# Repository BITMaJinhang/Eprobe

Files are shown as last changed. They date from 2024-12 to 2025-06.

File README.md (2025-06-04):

# [Eprobe] Engineering Files Repository  

This repository contains engineering files for a multi-platform system, organized by functional modules to facilitate project management and collaboration.  

## Directory Structure and Descriptions  

### 1. Hardware/  
- **Content**: Hardware design engineering files  
- **Includes**:  
  - BOM — Bill of Materials (component models and quantities)  
  - PCB — PCB design diagrams  
  - Schematics — Circuit schematic diagrams  
  - 3DShell — 3D casing source files  
- **Purpose**: Reference for hardware development and manufacturing  

### 2. BLE_CH582/  
- **Content**: CH582 coprocessor firmware project  
- **Includes**:  
  - APP/ — Core functional code directory  
  - All_EVT.zip/ — All functional examples for CH58x, including firmware libraries  
- **Development Tool**: MounRiver Studio  

### 3. MCU_STM32/  
- **Content**: STM32 main processor firmware project  
- **Includes**:  
  - EprobeSTAT_V4.zip — STM32CubeIDE full project file (zipped)  
  - Core/ — Core functional code directory  
- **Development Tool**: STM32CubeIDE  

### 4. MatLabApp/  
- **Content**: MATLAB PC application project  
- **Includes**:  
  - EprobeUART.mlapp — MATLAB App Designer project file  
  - code.m — Source code for the project  
- **Development Tool**: MATLAB R20A  

### 5. MobileAPP/  
- **Content**: Mobile application project  
- **Includes**:  
  - src/ — Application source code (Vue.js)  
  - quasar.config.js — Quasar framework configuration  
  - package.json — Dependency management file  
- **Technology Stack**: Quasar + Capacitor  

## Engineering File Organization Principles  
1. Each folder corresponds to an independent functional module with complete project configurations.  
2. Standard project file formats for each platform are adopted.  
3. Hardware and software files are separated to enable collaborative development.  

## Quick Access  
- Hardware design: Directly view PDF diagrams in `Hardware/`.  
- Firmware development: Open project files via the corresponding IDE.  
- PC application debugging: Run projects as required by each platform tool.

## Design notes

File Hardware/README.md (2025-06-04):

# Hardware Design Documentation

This folder contains hardware design documentation for [Eprobe], providing supplementary information to the main thesis.

## Contents

1. **BOM File**  
   - File: [BOM_EprobeV3_2].xlsx  
   - Description: Detailed list of all hardware components, including part numbers, quantities, suppliers, and specifications.

2. **Schematic Diagram**  
   - File:
   - [SCH_EprobeV3_2_1-P1.MCU].pdf
   - [SCH_EprobeV3_2_2-P2.Power].pdf
   - [SCH_EprobeV3_2_3-P3.ADDA].pdf
   - [SCH_EprobeV3_2_4-P4.TIA_1].pdf
   - [SCH_EprobeV3_2_5-P4.TIA_2].pdf
   - [SCH_EprobeV3_2_6-P4.TIA_3].pdf
   - Description: Circuit design schematic showing component connections and signal flow.

3. **PCB Layout**  
   - File:
   - [Top Layer].pdf  
   - [Bottom Layer].pdf  
   - [Assy_Top].pdf  
   - [Assy_Bottom].pdf  
   - [Int. Plane 1].pdf  
   - [Int. Plane 2].pdf  
   - Description: Printed Circuit Board layout showing top and bottom layer traces, vias, and component placement.

4. **EasyEDA Project Files**  
   - Files: [ProDoc_Eprobe_V3_1].epro  
   - Description: Original design files created with EasyEDA, including schematic and PCB layout projects. These files can be imported into EasyEDA for editing or modification.

## Usage Instructions

1. **BOM File**  
   - Open with Microsoft Excel or compatible software.  
   - Use for procuring all necessary electronic components.

2. **Schematic Diagram**  
   - Provides detailed circuit design.  
   - Useful for analyzing circuit operation or making modifications.

3. **PCB Layout**  
   - Shows the physical arrangement of the final PCB.  
   - Helps understand component placement and board dimensions.

4. **EasyEDA Project Files**  
   - Download and import into [EasyEDA](https://pro.lceda.cn) for editing.  
   - Requires an EasyEDA account (free tier available).

## Version Information

- Current Version: v3.2

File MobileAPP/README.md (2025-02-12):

# Mobile App Development Overview

This mobile app is developed using the **Vue-quasar-capacitor** framework, targeting mobile platforms. The development environment is set up on a **MacBook Air M1** running **macOS Sequoia 15.3.1**.

## Project Configuration

- **Framework**: Vue, Quasar, Capacitor
- **Development Platform**: macOS Sequoia 15.3.1 (MacBook Air M1)

### Key Plugins

The following plugins need to be manually installed for the project to function correctly:
- **@capacitor-community/bluetooth-le**
- **vue-chartjs**

Plugin and project configuration details are available in the following files:
- `package.json`
- `package-lock.json`

## Source Code

The main source code for the app is located in the `src` folder.

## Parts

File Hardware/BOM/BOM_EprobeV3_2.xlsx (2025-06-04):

No. | Quantity | Comment | Designator | Footprint | Value | Manufacturer Part | Manufacturer | Supplier Part | Supplier
1 | 2 | 2.2uF | C1,C5 | C0402 | 2.2uF | CL05A225MQ5NSNC | SAMSUNG(三星) | C12530 | LCSC
2 | 3 | 100nF | C2,C3,C4 | C0402 | 100nF | CC0402KRX7R7BB104 | YAGEO(国巨) | C60474 | LCSC
3 | 1 | 10nF | C14 | C0402 | 10nF
4 | 1 | 22nF | C15 | C0402 | 22nF
5 | 38 | 100nF | C16,C20,C24,C28,C38,C40,C44,C50,C51,C59,C74,C75,C76,C84,C85,C86,C89,C96,C104,C105,C106,C113,C114,C115,C116,C117,C125,C126,C127,C134,C135,C136,C137,C138,C141,C142,C145,C146 | C0402 | 100nF
6 | 1 | 10uF | C17 | C0402 | 10uF | CC0402KRX7R7BB104 | YAGEO(国巨) |  | LCSC
7 | 1 | 1uF | C18 | C0402 | 1uF | CC0402KRX7R7BB104 | YAGEO(国巨) |  | LCSC
8 | 1 | 220nF | C19 | C0402 | 220nF | CC0402KRX7R7BB104 | YAGEO(国巨) |  | LCSC
9 | 6 | 33nF | C21,C60,C110,C131,C139,C143 | C0402 | 33nF
10 | 4 | 18pF | C22,C23,C72,C73 | C0402 | 18pF
11 | 12 | 100pF | C27,C31,C61,C62,C103,C111,C112,C124,C132,C133,C140,C144 | C0402 | 100pF
12 | 1 | 12pF | C45 | C0402 | 12pF | CL05A475MP5NRNC | SAMSUNG(三星) |  | LCSC
13 | 1 | 12pF | C46 | C0402 | 12pF | 0402CG120J500NT | FH(风华) | C1547 | LCSC
14 | 4 | 100nF | C47,C48,C63,C64 | C0402 | 100nF | CL05B104KB54PNC | SAMSUNG(三星) | C307331 | LCSC
15 | 1 | 4.7uF | C49 | C0402 | 4.7uF | CL05A475MP5NRNC | SAMSUNG(三星) | C23733 | LCSC
16 | 2 | 10uF | C65,C77 | C0402 | 10uF
17 | 5 | 10uF | C147,C148,C149,C150,C151 | C0402 | 10uF | CL05A106MQ5NUNC | SAMSUNG(三星) | C15525 | LCSC
18 | 7 | 10nF | C152,C153,C154,C155,C156,C157,C158 | C0402 | 10nF | CL05B103KB5NNNC | SAMSUNG(三星) | C15195 | LCSC
19 | 12 | 10uF | C159,C160,C161,C162,C163,C164,C165,C166,C167,C168,C169,C170 | C0603 | 10uF | GRM188R61E106KA73D | muRata(村田) | C344022 | LCSC
20 | 2 | 1uF | C173,C174 | C0402 | 1uF | GRM155R61H105KE05D | muRata(村田) | C1518208 | LCSC
21 | 1 | 22uF | C176 | C0402 | 22uF | GRM158R61A226ME15D | muRata(村田) | C3845593 | LCSC
22 | 6 | PJ-320D | CN3,CN4,CN5,CN6,CN7,CN8 | AUDIO-SMD_PJ-320D |  | PJ-320D | SHOU HAN(首韩) | C431535 | LCSC
23 | 9 | HC-1.0-4PWT | CN9,CN10,CN11,CN12,CN13,CN14,CN16,CN17,CN18 | CONN-SMD_4P-P1.00_HCTL_HC-1.0-4PWT |  | HC-1.0-4PWT | HCTL(华灿天禄) | C2845363 | LCSC
24 | 12 | NUP2105LT1G | D5,D6,D13,D14,D15,D16,D17,D18,D19,D20,D21,D22 | SOT-23-3_L2.9-W1.3-P1.90-LS2.4-BR |  | NUP2105LT1G | TECH PUBLIC(台舟) | C2890118 | LCSC
25 | 5 | 1N5819WS | D23,D24,D25,D26,D27 | SOD-323_L1.8-W1.3-LS2.5-RD |  | 1N5819WS | Hottech(合科泰) | C191023 | LCSC
26 | 1 | SRV05-4 | D28 | SOT-23-6_L2.9-W1.6-P0.95-LS2.8-BL-1 |  | SRV05-4 | 宏迦橙 | C7420376 | LCSC
27 | 4 | BLM18AG601SN1D | L1,L2,L4,L6 | L0603 |  | BLM18AG601SN1D | muRata(村田) | C19330 | LCSC
28 | 2 | 10uH | L9,L10 | IND-SMD_L4.4-W4.2_BCIHP0412SC | 10uH | BCIHP0420SC-100M | BC(台湾诚阳) | C2921170 | LCSC
29 | 1 | LED_0603-R | LED2 | LED_0603
30 | 1 | LED_0603-G | LED3 | LED_0603
31 | 2 | NCD0603G1 | LED4,LED6 | LED0603-RD |  | NCD0603G1 | 国星光电 | C84267 | LCSC
32 | 1 | NCD0603B1 | LED5 | LED0603-RD |  | NCD0603B1 | 国星光电 | C84266 | LCSC
33 | 1 | AO3401A | Q1 | SOT-23_L2.9-W1.3-P1.90-LS2.4-BR |  | AO3401A | AOS | C15127 | LCSC
34 | 13 | 10kΩ | R2,R3,R16,R53,R55,R100,R103,R132,R133,R141,R142,R171,R172 | R0402 | 10kΩ
35 | 2 | 390K | R5,R9 | R0402 | 390K
36 | 1 | 33K | R6 | R0402 | 33K
37 | 1 | 3.1kΩ | R17 | R0402 | 3.1kΩ
38 | 6 | 750Ω | R18,R94,R140,R179,R183,R187 | R0402 | 750Ω
39 | 12 | 2kΩ | R19,R20,R63,R87,R134,R135,R173,R174,R180,R181,R184,R185 | R0402 | 2kΩ
40 | 1 | 10kΩ | R24 | R0402 | 10kΩ | 0402WGF1003TCE | UNI-ROYAL(厚声) |  | LCSC
41 | 1 | 100Ω | R26 | R0402 | 100Ω
42 | 11 | 10K | R27,R43,R59,R60,R65,R66,R239,R242,R245,R248,R251 | R0402 | 10K
43 | 6 | 3.9K | R28,R240,R243,R246,R249,R252 | R0402 | 3.9K
44 | 6 | 2K | R29,R241,R244,R247,R250,R253 | R0402 | 2K
45 | 7 | 2.2K | R30,R42,R93,R139,R178,R182,R186 | R0402 | 2.2K
46 | 3 | 5.1K | R39,R40,R41 | R0402 | 5.1K
47 | 1 | 4.7K | R49 | R0402 | 4.7K
48 | 1 | 15K | R50 | R0402 | 15K
49 | 1 | 33kΩ | R54 | R0402 | 33kΩ | 0402WGF1542TCE | UNI-ROYAL(厚声) |  | LCSC
50 | 1 | 51kΩ | R56 | R0402 | 51kΩ | 0402WGF1203TCE | UNI-ROYAL(厚声) |  | LCSC
51 | 1 | 2kΩ | R57 | R0402 | 2kΩ | RC0402FR-075KL | YAGEO(国巨) |  | LCSC
52 | 1 | 10kΩ | R58 | R0402 | 10kΩ | RC0402FR-0710KL | YAGEO(国巨) | C60490 | LCSC
53 | 1 | 33kΩ | R61 | R0402 | 33kΩ
54 | 1 | 3.9kΩ | R62 | R0402 | 3.9kΩ
55 | 3 | 5.1kΩ | R64,R188,R189 | R0402 | 5.1kΩ | 0402WGF1003TCE | UNI-ROYAL(厚声) |  | LCSC
56 | 6 | 1kΩ | R190,R212,R218,R224,R230,R236 | R0402 | 1kΩ | 0402WGF5101TCE | UNI-ROYAL(厚声) |  | LCSC
57 | 6 | 10kΩ | R191,R213,R219,R225,R231,R237 | R0402 | 10kΩ | 0402WGF2202TCE | UNI-ROYAL(厚声) |  | LCSC
58 | 6 | 750Ω | R192,R214,R220,R226,R232,R238 | R0402 | 750Ω | 0402WGF2001TCE | UNI-ROYAL(厚声) |  | LCSC
59 | 1 | 0 | R208 | R0402 | 0
60 | 1 | TS-1088R-02026 | SW1 | SW-SMD_L3.9-W3.0-P4.45 |  | TS-1088R-02026 | XUNPU(讯普) | C455280 | LCSC
61 | 1 | MSK12C02 | SW3 | SW-TH_MSK12C02 |  | MSK12C02 | SHOU HAN(首韩) | C431540 | LCSC
62 | 1 | TS-1088-AR02016 | SW4 | SW-SMD_L3.9-W3.0-P4.45 |  | TS-1088-AR02016 | XUNPU(讯普) | C720477 | LCSC
63 | 2 | M2螺丝 | TP1,TP2 | M2螺丝
64 | 1 | CH582F | U1 | QFN-28_L4.0-W4.0-P0.40-BL-EP2.8 |  | CH582F | WCH(南京沁恒) | C3001175 | LCSC
65 | 1 | STM32L432KCU6 | U2 | UFQFPN-32_L5.0-W5.0-P0.50-TL-EP3.5 |  | STM32L432KCU6 | ST(意法半导体) | C1337280 | LCSC
66 | 1 | DAC8568ICPWR | U3 | TSSOP-16_L5.0-W4.4-P0.65-LS6.4-BL |  | DAC8568ICPWR | TI(德州仪器) | C524819 | LCSC
67 | 1 | DG409DQ-T1-E3 | U4 | TSSOP-16_L5.0-W4.4-P0.65-LS6.4-BL |  | DG409DQ-T1-E3 | VISHAY(威世) | C2673358 | LCSC
68 | 6 | OPA4197QPWRQ1 | U6,U7,U8,U9,U16,U41 | TSSOP-14_L5.0-W4.4-P0.65-LS6.4-BL |  | OPA4197QPWRQ1 | TI(德州仪器) | C4366710 | LCSC
69 | 1 | TP4056 | U12 | ESOP-8_L4.9-W3.9-P1.27-LS6.0-BL-EP |  | TP4056 | UMW(友台半导体) | C725790 | LCSC
70 | 1 | SGM2036-3.3YN5G/TR | U15 | SOT-23-5_L3.0-W1.7-P0.95-LS2.8-BR |  | SGM2036-3.3YN5G/TR | SGMICRO(圣邦微) | C92402 | LCSC
71 | 2 | ADS1256IDBR | U20,U30 | SSOP-28_L10.2-W5.3-P0.65-LS7.8-BL |  | ADS1256IDBR | TI(德州仪器) | C28186 | LCSC
72 | 1 | 嘉立创二维码5x5 | U21 | JLC-QRCODE-5x5
73 | 2 | MT3608L | U22,U27 | SOT-23-6_L2.9-W1.7-P0.95-LS2.8-BL |  | MT3608L | 西安航天民芯 | C2932326 | LCSC
74 | 2 | TPS7A4901DGNT | U25,U26 | MSOP-8_L3.0-W3.0-P0.65-LS4.9-BL-EP1.8 |  | TPS7A4901DGNT | TI(德州仪器) | C61422 | LCSC
75 | 1 | TPS7A3001DGNR | U28 | MSOP-8_L3.0-W3.0-P0.65-LS5.0-BL-EP |  | TPS7A3001DGNR | TI(德州仪器) | C33835 | LCSC
76 | 1 | BWU.FL-IPEX1 | U29 | IPEX-SMD_BWIPX-1-001E |  | BWU.FL-IPEX1 | BAT WIRELESS(蝙蝠无线) | C5137195 | LCSC
77 | 1 | REF5025AIDR | U31 | SOIC-8_L4.9-W3.9-P1.27-LS6.0-BL |  | REF5025AIDR | TI(德州仪器) | C11341 | LCSC
78 | 1 | 32MHz | U42 | CRYSTAL-SMD_4P-L2.0-W1.6-BL-2 | 32MHz | XL7EL89COI-111YLC-32M | YXC(扬兴晶振) | C2965584 | LCSC
79 | 1 | WAFER-SH1.0-2PWB | U43 | CONN-SMD_2P-P1.00_XUNPU_WAFER-SH1.0-2PWB |  | WAFER-SH1.0-2PWB | XUNPU(讯普) | C3029341 | LCSC
80 | 1 | WAFER-SH1.0-3PWB | U44 | CONN-SMD_3P-P1.00_WAFER-SH1.0-3PWB |  | WAFER-SH1.0-3PWB | XUNPU(讯普) | C3029342 | LCSC
81 | 1 | KH-TYPE-C-16P | USB1 | USB-C-SMD_KH-TYPE-C-16P |  | KH-TYPE-C-16P | kinghelm(金航标) | C709357 | LCSC
82 | 2 | 8MHz | X5,X7 | OSC-SMD_4P-L3.2-W2.5-BL | 8MHz | X32258MOB4SI | YXC(扬兴晶振) | C2682775 | LCSC
83 | 1 | 32.768kHz | X6 | OSC-SMD_L3.2-W1.5 | 32.768kHz | X321532768KGD2SI | YXC(扬兴晶振) | C620155 | LCSC

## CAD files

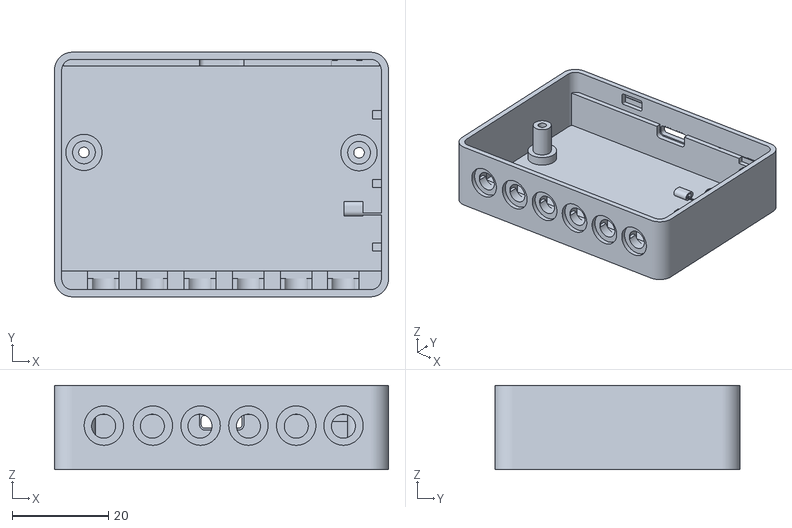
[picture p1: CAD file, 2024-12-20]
Hardware/3DShell_EprobeV3_1/3DShell_Eprobe_V3_1_B.stl
69.6 x 51.0 x 17.5

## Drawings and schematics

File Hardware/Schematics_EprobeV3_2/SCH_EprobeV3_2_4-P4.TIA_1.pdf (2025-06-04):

# S4b 10 S3b 11 S2b 12 S1b 13 V+ 14 GND 15 A1 16

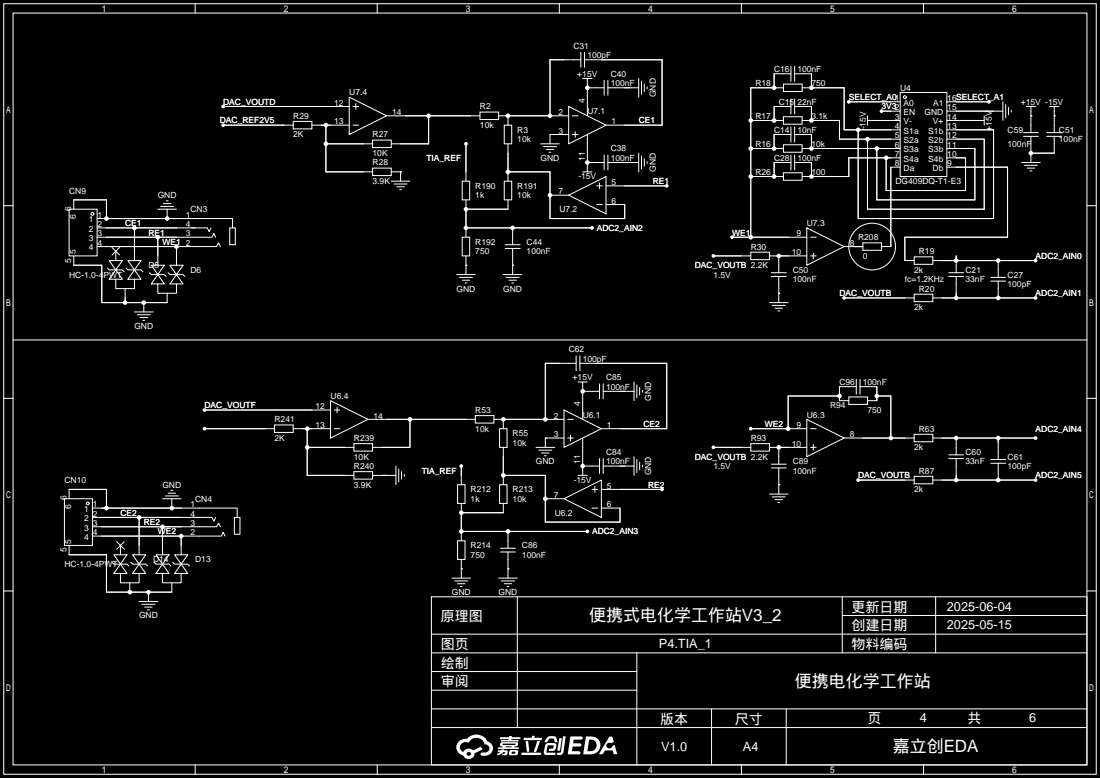
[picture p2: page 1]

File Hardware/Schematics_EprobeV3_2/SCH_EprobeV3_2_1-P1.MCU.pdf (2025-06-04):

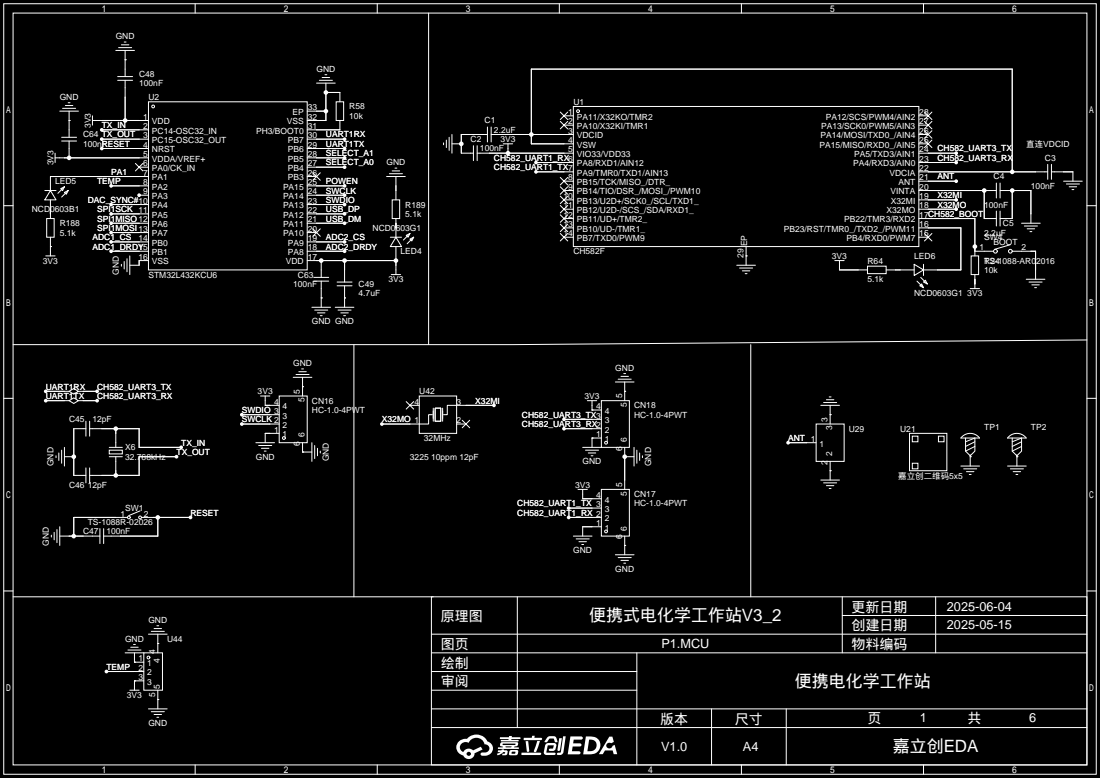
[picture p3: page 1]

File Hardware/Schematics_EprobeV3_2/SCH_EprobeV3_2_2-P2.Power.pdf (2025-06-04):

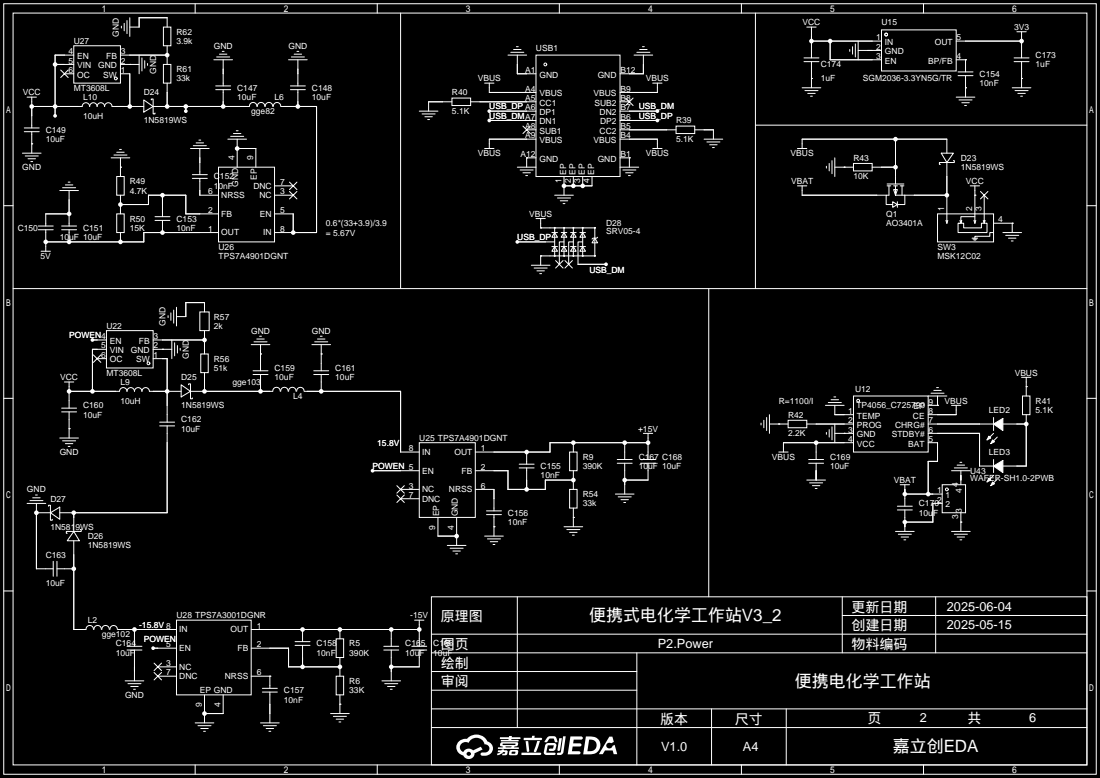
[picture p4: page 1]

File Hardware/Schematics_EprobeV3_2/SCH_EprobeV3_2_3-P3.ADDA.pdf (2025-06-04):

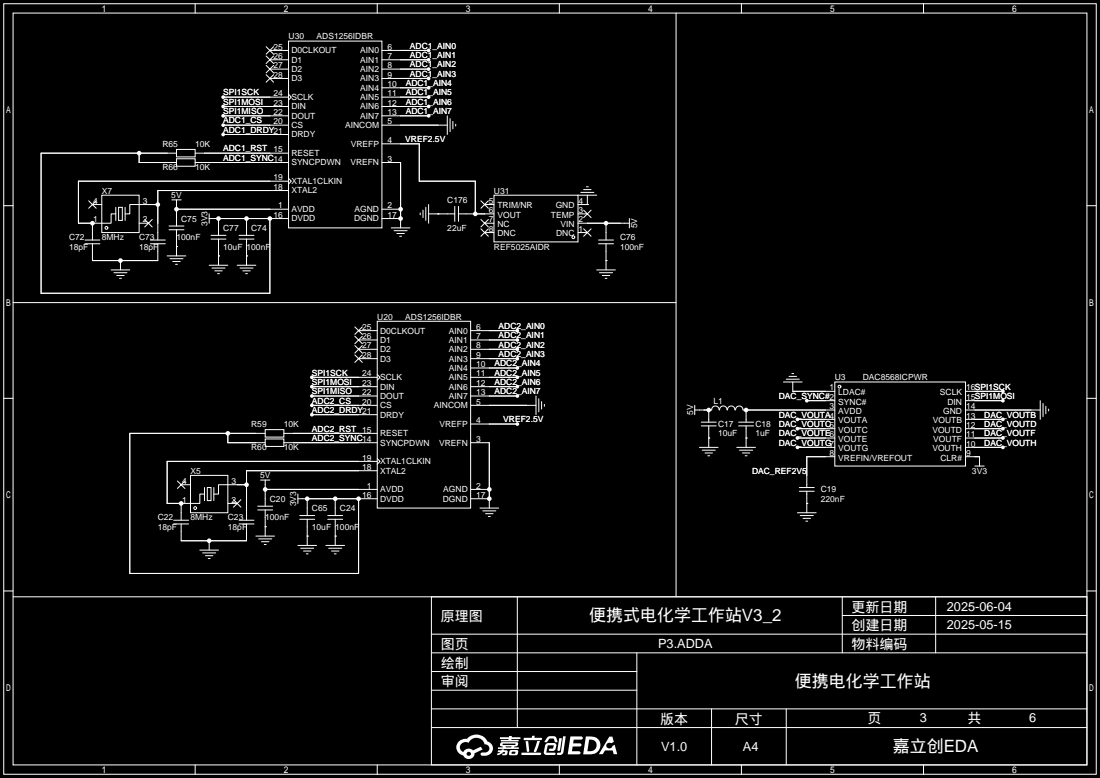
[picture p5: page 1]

VOUTH 10 VOUTF 11 VOUTD 12 VOUTB 13 GND 14 DIN 15 SCLK 16

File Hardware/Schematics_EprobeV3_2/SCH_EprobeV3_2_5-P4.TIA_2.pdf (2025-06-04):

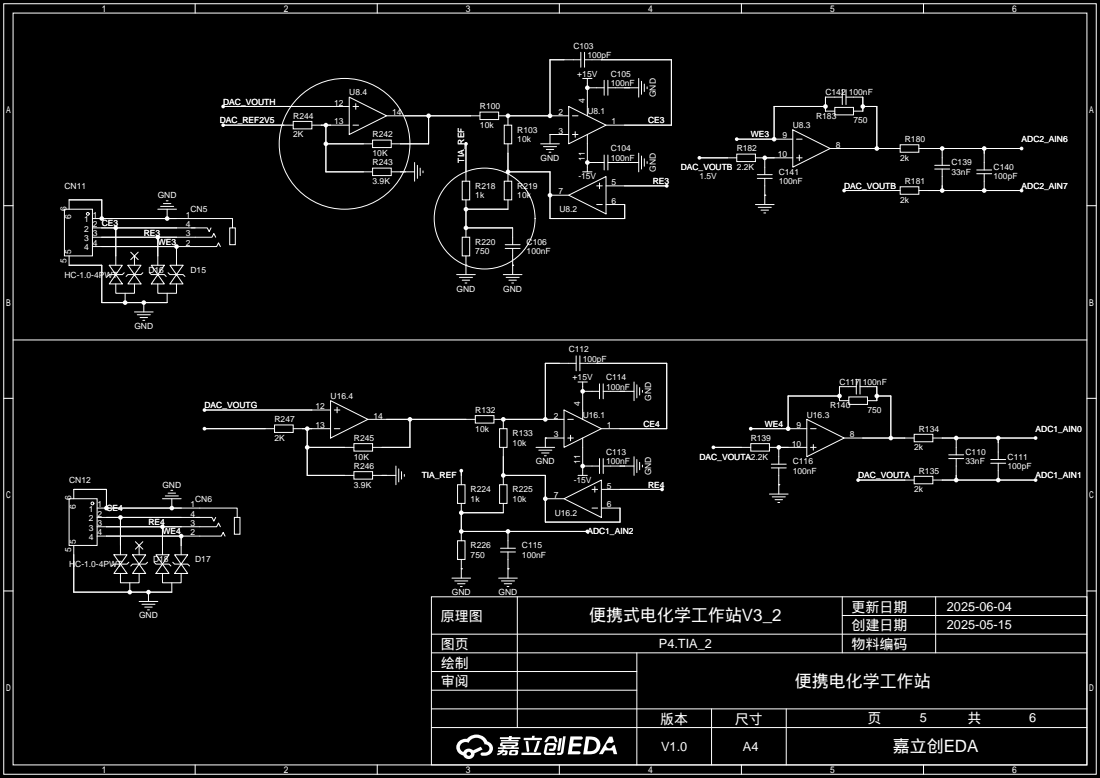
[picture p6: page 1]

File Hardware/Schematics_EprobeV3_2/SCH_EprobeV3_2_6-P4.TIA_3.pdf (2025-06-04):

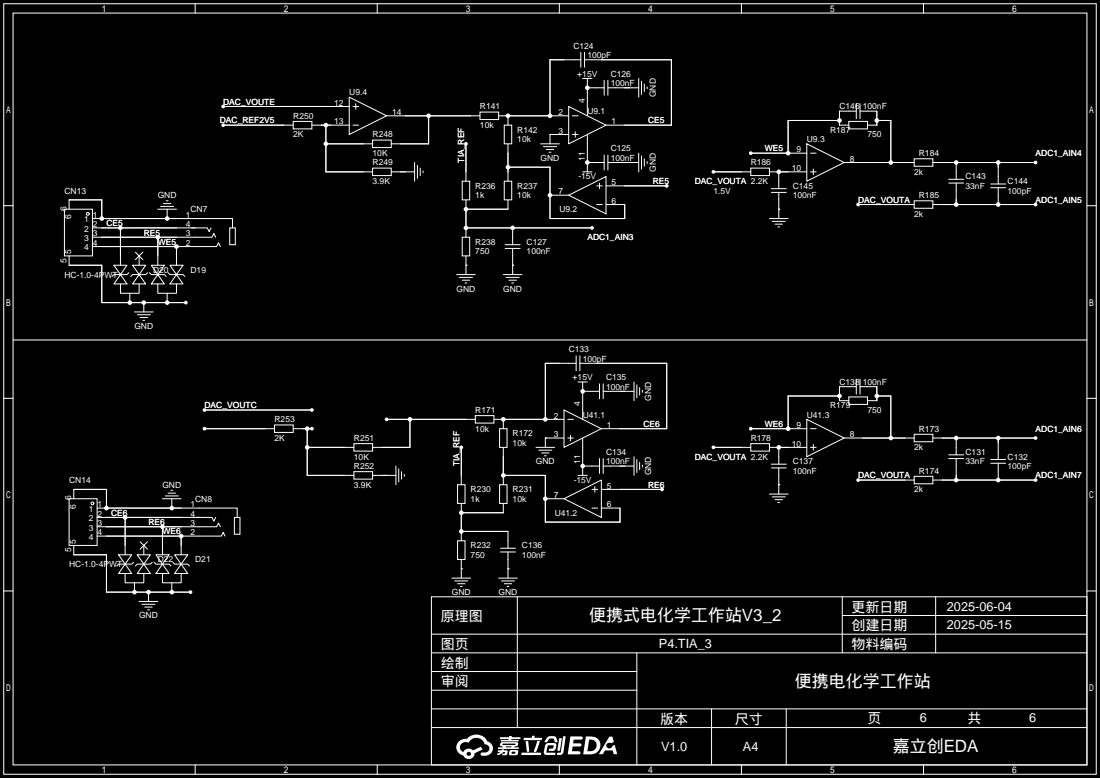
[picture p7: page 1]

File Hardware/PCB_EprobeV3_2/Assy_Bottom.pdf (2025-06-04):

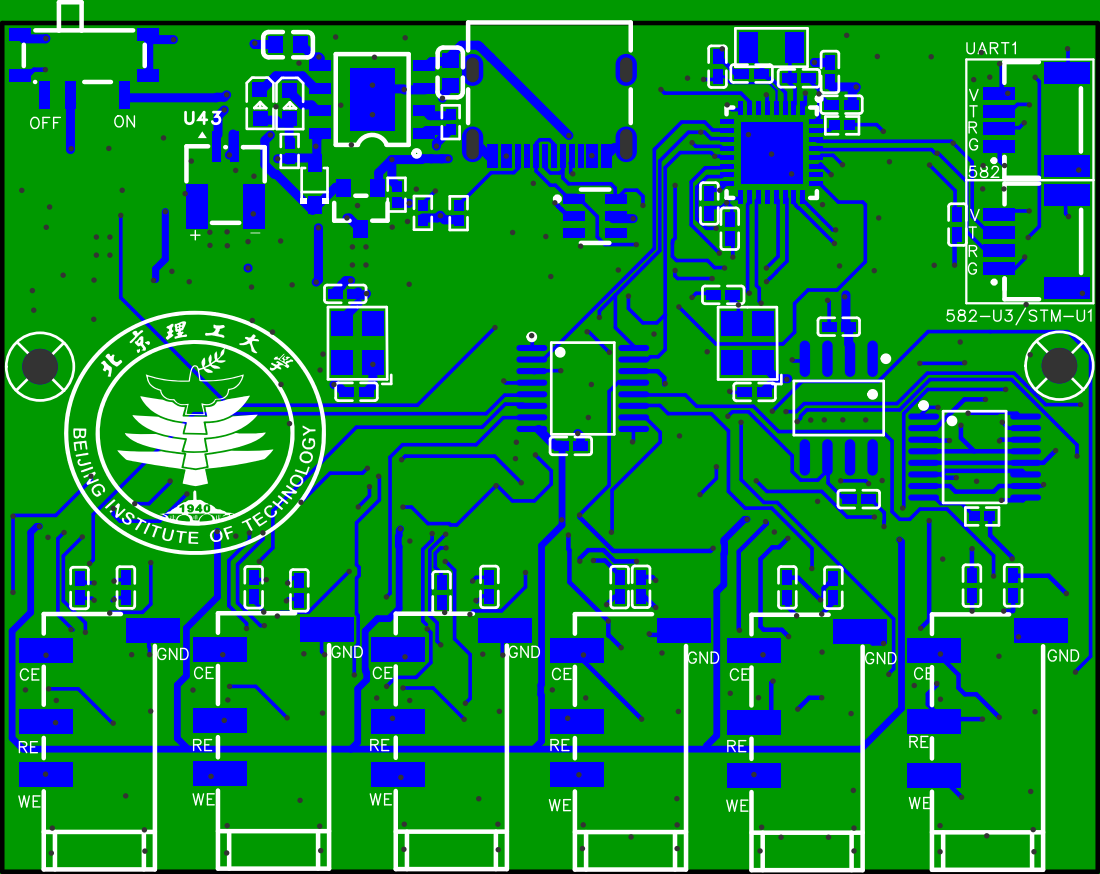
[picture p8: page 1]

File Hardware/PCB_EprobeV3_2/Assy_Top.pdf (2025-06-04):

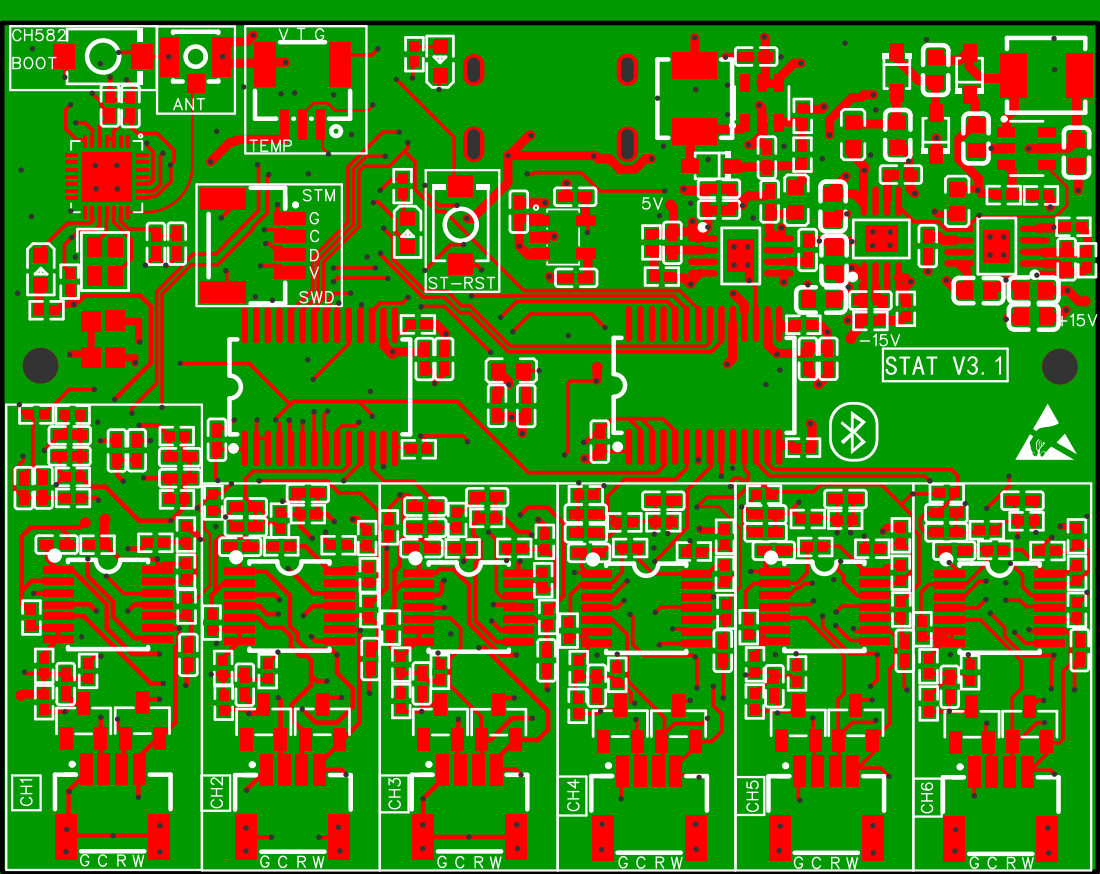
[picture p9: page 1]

CH582 BOOT | ANT | V G T

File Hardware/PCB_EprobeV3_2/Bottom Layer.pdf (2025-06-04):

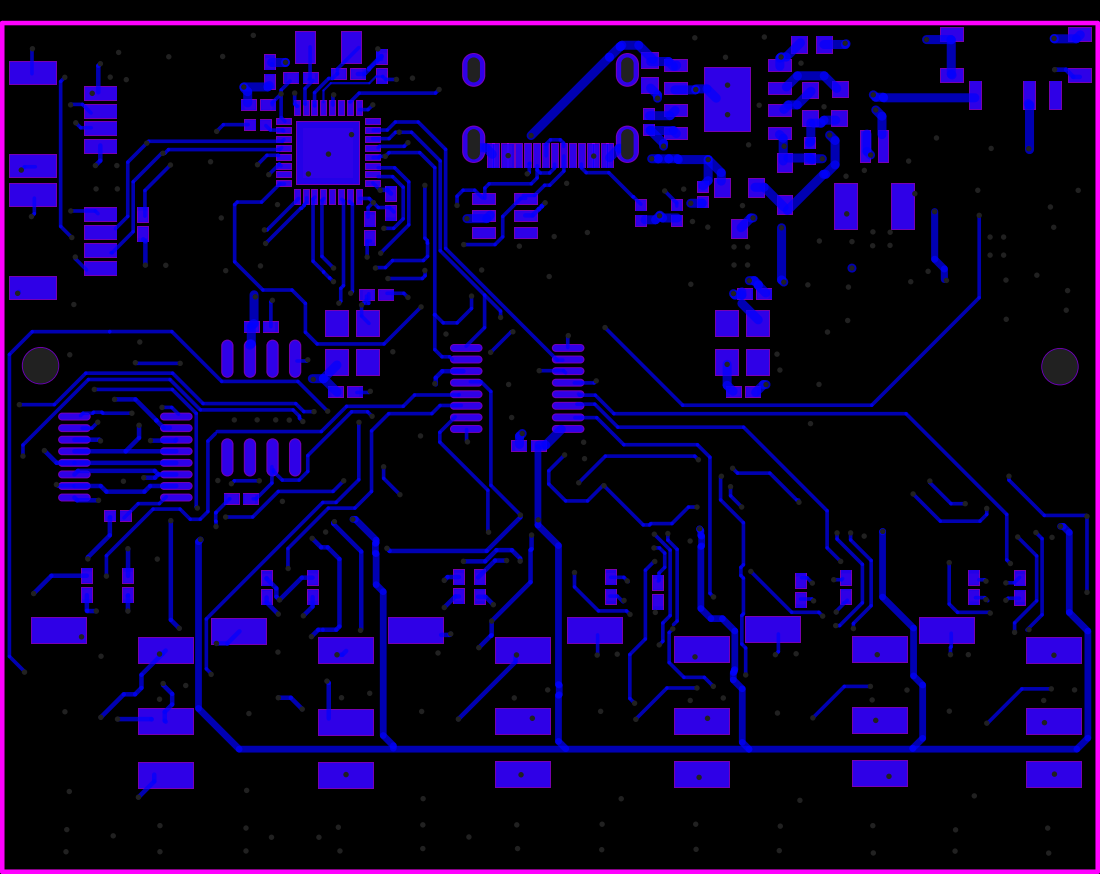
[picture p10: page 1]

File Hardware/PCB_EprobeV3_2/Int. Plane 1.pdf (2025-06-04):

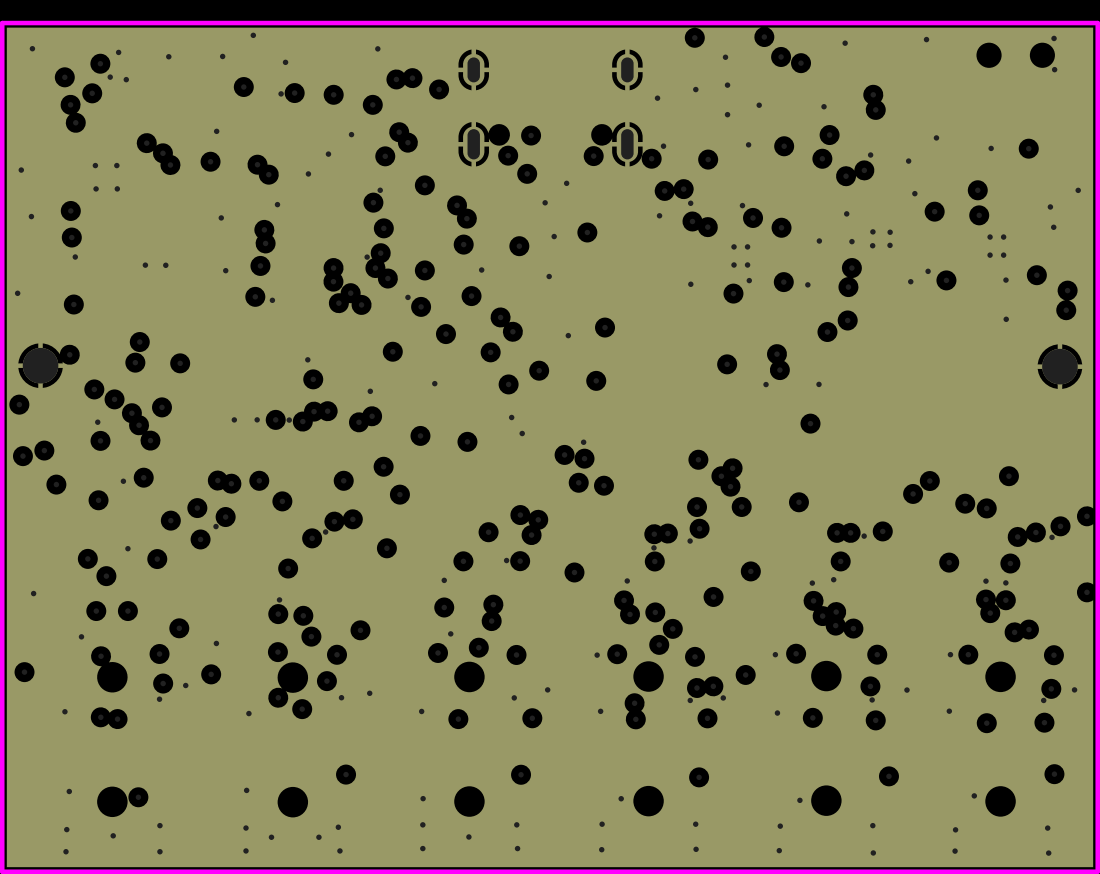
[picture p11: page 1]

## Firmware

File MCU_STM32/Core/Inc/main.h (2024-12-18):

/* USER CODE BEGIN Header */
/**
  ******************************************************************************
  * @file           : main.h
  * @brief          : Header for main.c file.
  *                   This file contains the common defines of the application.
  ******************************************************************************
  * @attention
  *
  * Copyright (c) 2024 STMicroelectronics.
  * All rights reserved.
  *
  * This software is licensed under terms that can be found in the LICENSE file
  * in the root directory of this software component.
  * If no LICENSE file comes with this software, it is provided AS-IS.
  *
  ******************************************************************************
  */
/* USER CODE END Header */

/* Define to prevent recursive inclusion -------------------------------------*/
#ifndef __MAIN_H
#define __MAIN_H

#ifdef __cplusplus
extern "C" {
#endif

/* Includes ------------------------------------------------------------------*/
#include "stm32l4xx_hal.h"

/* Private includes ----------------------------------------------------------*/
/* USER CODE BEGIN Includes */
#if defined(STM32F1)
#include "stm32f1xx_hal.h"
#include "stm32f1xx_hal_spi.h"
#elif defined(STM32F4)
#include "stm32f4xx_hal.h"
#include "stm32f4xx_hal_spi.h"
#elif defined(STM32L4)
#include "stm32l4xx_hal.h"
#include "stm32l4xx_hal_spi.h"
#include "stm32l4xx_hal_dma.h"
#elif defined(STM32F3)
#include "stm32f3xx_hal.h"
#include "stm32f3xx_hal_spi.h"
#endif
#include <stdint.h>
#include <stdio.h>
#include <stdlib.h>
#include <stdbool.h>
#include <math.h>
#include <string.h>
#include "ads125x.h"
#include "dac856x.h"
#include "eprobe.h"
#include "ble.h"
#include "ds18b20.h"

/* USER CODE END Includes */

/* Exported types ------------------------------------------------------------*/
/* USER CODE BEGIN ET */

/* USER CODE END ET */

/* Exported constants --------------------------------------------------------*/
/* USER CODE BEGIN EC */

/* USER CODE END EC */

/* Exported macro ------------------------------------------------------------*/
/* USER CODE BEGIN EM */

/* USER CODE END EM */

/* Exported functions prototypes ---------------------------------------------*/
void Error_Handler(void);

/* USER CODE BEGIN EFP */

/* USER CODE END EFP */

/* Private defines -----------------------------------------------------------*/
#define LED_Pin GPIO_PIN_1
#define LED_GPIO_Port GPIOA
#define TEMP_Pin GPIO_PIN_2
#define TEMP_GPIO_Port GPIOA
#define DAC_SYNC__Pin GPIO_PIN_4
#define DAC_SYNC__GPIO_Port GPIOA
#define ADC1_CS_Pin GPIO_PIN_0
#define ADC1_CS_GPIO_Port GPIOB
#define ADC1_DRDY_Pin GPIO_PIN_1
#define ADC1_DRDY_GPIO_Port GPIOB
#define ADC2_DRDY_Pin GPIO_PIN_8
#define ADC2_DRDY_GPIO_Port GPIOA
#define ADC2_CS_Pin GPIO_PIN_9
#define ADC2_CS_GPIO_Port GPIOA
#define POWEN_Pin GPIO_PIN_15
#define POWEN_GPIO_Port GPIOA
#define SELECT_A0_Pin GPIO_PIN_4
#define SELECT_A0_GPIO_Port GPIOB
#define SELECT_A1_Pin GPIO_PIN_5
#define SELECT_A1_GPIO_Port GPIOB

/* USER CODE BEGIN Private defines */

/* USER CODE END Private defines */

#ifdef __cplusplus
}
#endif

#endif /* __MAIN_H */

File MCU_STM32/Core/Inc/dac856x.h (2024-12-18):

/*
 * dac856x.h
 *
 *  Created on: Sep 26, 2024
 *      Author: MaJinhang
 */

#ifndef INCLUDE_DAC856X_H_
#define INCLUDE_DAC856X_H_

//#define DEBUG_DAC856X	1

#define STM32L4

#if defined(STM32F1)
#include "stm32f1xx_hal.h"
#include "stm32f1xx_hal_spi.h"
#elif defined(STM32F4)
#include "stm32f4xx_hal.h"
#include "stm32f4xx_hal_spi.h"
#elif defined(STM32L4)
#include "stm32l4xx_hal.h"
#include "stm32l4xx_hal_spi.h"
#elif defined(STM32F3)
#include "stm32f3xx_hal.h"
#include "stm32f3xx_hal_spi.h"
#endif

// ref: https://github.com/imcort-nrf-drivers/dac8568

#define DAC856X_DEFAULT 0x0
#define DAC856X_SYNC_Port GPIOA
#define DAC856X_SYNC_Pin GPIO_PIN_4
#define DAC856X_VREF 2.5
#define DAC856X_GAIN_1 1
#define DAC856X_GAIN_2 2	//Gain = 1 for A/B grades or 2 for C/D grades

typedef union {
  uint32_t raw;
  uint8_t byte[4];
  struct {
    // LSB
    unsigned int feature : 4;
    unsigned int data : 16;
    unsigned int address : 4;
    unsigned int control : 4;
    unsigned int prefix : 4;
    // MSB
  } field;
} dac856x_reg_t;


typedef enum CHANNEL_SELECT {
  DAC_CH_A,
  DAC_CH_B,
  DAC_CH_C,
  DAC_CH_D,
  DAC_CH_E,
  DAC_CH_F,
  DAC_CH_G,
  DAC_CH_H,
  DAC_NO_MSG,
  DAC_BROADCAST
} CHANNEL_SELECT;

typedef enum {
  CONTROL_WRITE_TO_INPUT_REGISTER,
  CONTROL_UPDATE_DAC_REGISTER,
  CONTROL_WRITE_TO_DAC_CH_AND_UPDATE_ALL_REG,
  CONTROL_WRITE_TO_DAC_CH_AND_UPDATE_SINGLE_REG,
  CONTROL_POWER_DOWN_COMM,
  CONTROL_WRITE_TO_CLEAR_CODE_REG,
  CONTROL_WRITE_TO_LDAC_REG,
  CONTROL_SOFTWARE_RESET,
} CONTROL_TYPE;

typedef enum {
  CONTROL_SETUP_STATIC_MODE = 8,
  CONTROL_SETUP_FLEX_MODE = 9
} CONTROL_SETUP_MODE;

typedef enum {
  FEATURE_CLEAR_TO_ZERO_SCALE,
  FEATURE_CLEAR_TO_MID_SCALE,
  FEATURE_CLEAR_TO_FULL_SCALE,
  FEATURE_IGNORE_CLR_PIN
} CLEAR_CODE_FEATURE;

typedef enum {
  FEATURE_POWER_DOWN_INT_REF_STATIC,
  FEATURE_POWER_UP_INT_REF_STATIC,
  FEATURE_POWER_UP_INT_REF_FLEX = 0,
  FEATURE_POWER_UP_INT_REF_ALWAYS_FLEX = 0,
  FEATURE_POWER_DOWN_INT_REF_FLEX = 0,
  FEATURE_SWITCH_FROM_FLEX_TO_STATIC = 0
} INTERNAL_REF_COMM_FEATURE;

typedef enum {
  LDAC_REG_A = 1,
  LDAC_REG_B = 2,
  LDAC_REG_C = 4,
  LDAC_REG_D = 8,
  LDAC_REG_E = 16,
  LDAC_REG_F = 32,
  LDAC_REG_G = 64,
  LDAC_REG_H = 128
} WRITE_TO_LDAC_CH;

typedef enum {
  POWER_DAC_A = 1,
  POWER_DAC_B = 2,
  POWER_DAC_C = 4,
  POWER_DAC_D = 8,
  POWER_DAC_E = 16,
  POWER_DAC_F = 32,
  POWER_DAC_G = 64,
  POWER_DAC_H = 128
} POWER_UP_DOWN_CH;

typedef enum {
  POWER_UP_DAC = 0,
  POWER_DOWN_DAC_1KO_TO_GND = 16,
  POWER_DOWN_DAC_100KO_TO_GND = 32,
  POWER_DOWN_DAC_HIZ_TO_GND = 48
} POWER_UP_DOWN_DAC;

typedef enum {
  DATA_POWER_DOWN_INT_REF_STATIC = 0,
  DATA_POWER_UP_INT_REF_STATIC = 0,
  DATA_POWER_UP_INT_REF_FLEX = 32768,
  DATA_POWER_UP_INT_REF_ALWAYS_FLEX = 40960,
  DATA_POWER_DOWN_INT_REF_FLEX = 49152,
  DATA_SWITCH_FROM_FLEX_TO_STATIC = 0
} INTERNAL_REF_COMM_DATA;


// Struct "Object"
typedef struct {
	SPI_HandleTypeDef *hspix;
    GPIO_TypeDef *csPort;
    uint16_t     csPin;
    dac856x_reg_t	reg;
    uint8_t		gain;
} DAC856X_t;


uint8_t DAC856X_init(DAC856X_t *dac ,SPI_HandleTypeDef *hspi, uint8_t gain);
uint8_t DAC856X_CS(DAC856X_t *dac, uint8_t on);
uint8_t DAC856X_Write_Dac(DAC856X_t *dac, CHANNEL_SELECT chn, uint16_t val);
uint8_t DAC856X_Write_Dac_Voltage(DAC856X_t *dac, CHANNEL_SELECT chn, float val);
uint8_t DAC856X_Register_Write(DAC856X_t *dac);
#endif /* INCLUDE_DAC8568_H_ */

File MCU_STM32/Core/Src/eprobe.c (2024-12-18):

/*
 * eprobe.c
 *
 *  Created on: Jun 12, 2024
 *      Author: MaJinhang
 */

#include "main.h"

extern DAC856X_t dac1;
extern ADS125X_t adc1;
extern ADS125X_t adc2;
extern Eprobe_param_t RX_BUFFER;
extern uint32_t TimeTable;
extern SPI_HandleTypeDef hspi1;
extern UART_HandleTypeDef huart1;
extern UART_HandleTypeDef huart2;
extern UART_HandleTypeDef *huartGlobal; 


volatile uint8_t buffer_channel = Buffer_Channel_A;
volatile uint8_t buffer_index_a = 0;
volatile uint8_t buffer_index_b = 0;
float data_buffer_a[BUFFER_SIZE][3];
float data_buffer_b[BUFFER_SIZE][3];
extern StateMachine Machine[TOTAL_CHANNELS];

volatile uint8_t Loop_stop;

void State_Machine_Init(void){
  Machine[CHANNEL_1] = (StateMachine){.param.BLE.Channel = (float)CHANNEL_1,
	  	  	  	  	  	  	  	  	  .param.BLE.Mode = MODE_NONE,
                                      .timetable = 0,
                                      .DAC_CH = DAC_CH_D,
                                      .ADC_CH = ADS125X_CHANNEL_01,
									  .OCP_CH = ADS125X_CHANNEL_28,
                                      .adc = adc2,
                                      .Current_State = STATE_INIT,
									  .PauseFlag = 1,
  	  	  	  	  	  	  	  	  	  .StopFlag = 1};

  Machine[CHANNEL_2] = (StateMachine){.param.BLE.Channel = (float)CHANNEL_2,
	  	  	  	  	  	  	  	  	  .param.BLE.Mode = MODE_NONE,
                                      .timetable = 1,
                                      .DAC_CH = DAC_CH_F,
                                      .ADC_CH = ADS125X_CHANNEL_45,
									  .OCP_CH = ADS125X_CHANNEL_38,
                                      .adc = adc2,
                                      .Current_State = STATE_INIT,
									  .PauseFlag = 1,
  	  	  	  	  	  	  	  	  	  .StopFlag = 1};

  Machine[CHANNEL_3] = (StateMachine){.param.BLE.Channel = (float)CHANNEL_3,
	  	  	  	  	  	  	  	  	  .param.BLE.Mode = MODE_NONE,
                                      .timetable = 2,
                                      .DAC_CH = DAC_CH_H,
                                      .ADC_CH = ADS125X_CHANNEL_67,
                                      .adc = adc2,
                                      .Current_State = STATE_INIT,
									  .PauseFlag = 1,
  	  	  	  	  	  	  	  	  	  .StopFlag = 1};

  Machine[CHANNEL_4] = (StateMachine){.param.BLE.Channel = (float)CHANNEL_4,
	  	  	  	  	  	  	  	  	  .param.BLE.Mode = MODE_NONE,
                                      .timetable = 3,
                                      .DAC_CH = DAC_CH_G,
                                      .ADC_CH = ADS125X_CHANNEL_01,
									  .OCP_CH = ADS125X_CHANNEL_28,
                                      .adc = adc1,
                                      .Current_State = STATE_INIT,
									  .PauseFlag = 1,
  	  	  	  	  	  	  	  	  	  .StopFlag = 1};

  Machine[CHANNEL_5] = (StateMachine){.param.BLE.Channel = (float)CHANNEL_5,
	  	  	  	  	  	  	  	  	  .param.BLE.Mode = MODE_NONE,
                                      .timetable = 4,
                                      .DAC_CH = DAC_CH_E,
                                      .ADC_CH = ADS125X_CHANNEL_45,
									  .OCP_CH = ADS125X_CHANNEL_38,
                                      .adc = adc1,
                                      .Current_State = STATE_INIT,
									  .PauseFlag = 1,
  	  	  	  	  	  	  	  	  	  .StopFlag = 1};

  Machine[CHANNEL_6] = (StateMachine){.param.BLE.Channel = (float)CHANNEL_6,
	  	  	  	  	  	  	  	  	  .param.BLE.Mode = MODE_NONE,
                                      .timetable = 5,
                                      .DAC_CH = DAC_CH_C,
                                      .ADC_CH = ADS125X_CHANNEL_67,
                                      .adc = adc1,
                                      .Current_State = STATE_INIT,
									  .PauseFlag = 1,
  	  	  	  	  	  	  	  	  	  .StopFlag = 1};

}


float my_log(float datain) { return datain > 0 ? log10(datain) : log10(-datain); }

uint8_t LED_ON(void) {
  HAL_GPIO_WritePin(LED_PORT, LED_PIN, GPIO_PIN_RESET);
  return 0;
}
uint8_t LED_OFF(void) {
  HAL_GPIO_WritePin(LED_PORT, LED_PIN, GPIO_PIN_SET);
  return 0;
}
uint8_t LED_TOGGLE(void) {
  HAL_GPIO_TogglePin(LED_PORT, LED_PIN);
  return 0;
}
uint8_t Sensitivity_set(StateMachine *machine) {

  HAL_GPIO_WritePin(SENS_SELECTA0_Port, SENS_SELECTA0_Pin, GPIO_PIN_RESET);
  HAL_GPIO_WritePin(SENS_SELECTA1_Port, SENS_SELECTA1_Pin, GPIO_PIN_RESET);
  machine->R_SENS = 750.0;

  if(machine->param.BLE.Channel ==0 && machine->param.BLE.Mode!= MODE_OCPT)
  {
#if UART_DEBUG
//  printf("Sensitivity setting:\n");
#endif
  switch (machine->param.BLE.Sensitivity) {
  case SENSITIVITY_1: // 00
#if UART_DEBUG
//    printf("SENSITIVITY_1\n");
#endif
    HAL_GPIO_WritePin(SENS_SELECTA0_Port, SENS_SELECTA0_Pin, GPIO_PIN_RESET);
    HAL_GPIO_WritePin(SENS_SELECTA1_Port, SENS_SELECTA1_Pin, GPIO_PIN_RESET);
    machine->R_SENS = 750.0;
    break;
  case SENSITIVITY_2: // 10
#if UART_DEBUG
    printf("SENSITIVITY_2\n");
#endif
    HAL_GPIO_WritePin(SENS_SELECTA0_Port, SENS_SELECTA0_Pin, GPIO_PIN_SET);
    HAL_GPIO_WritePin(SENS_SELECTA1_Port, SENS_SELECTA1_Pin, GPIO_PIN_RESET);
    machine->R_SENS = 3100.0;
    break;
  case SENSITIVITY_3: // 01
#if UART_DEBUG
    printf("SENSITIVITY_3\n");
#endif
    HAL_GPIO_WritePin(SENS_SELECTA0_Port, SENS_SELECTA0_Pin, GPIO_PIN_RESET);
    HAL_GPIO_WritePin(SENS_SELECTA1_Port, SENS_SELECTA1_Pin, GPIO_PIN_SET);
    machine->R_SENS = 10000.0;
    break;
  case SENSITIVITY_4: //11
#if UART_DEBUG
    printf("SENSITIVITY_4\n");
#endif
    HAL_GPIO_WritePin(SENS_SELECTA0_Port, SENS_SELECTA0_Pin, GPIO_PIN_SET);
    HAL_GPIO_WritePin(SENS_SELECTA1_Port, SENS_SELECTA1_Pin, GPIO_PIN_SET);
    machine->R_SENS = 100.0;
    break;
  default:
#if UART_DEBUG
    printf("error:wrong in Sensitivity_set.\n");
#endif
    break;
  }
  }
  return 0;
}
uint8_t Set_VBias(StateMachine *machine, float vbias) {
	float Calibrated_Vbias = vbias;
//	Calibrated_Vbias = machine->Cali_Vbias;
	switch (machine->param.BLE.Channel){
	case CHANNEL_1:
		Calibrated_Vbias = (vbias - 0.0241)/0.9968;
		break;
	case CHANNEL_2:
		Calibrated_Vbias = (vbias - 0.0148)/1.0011;
		break;
	case CHANNEL_3:
		Calibrated_Vbias = (vbias - 0.018)/1.0034;
		break;
	case CHANNEL_4:
		Calibrated_Vbias = (vbias - 0.0065)/1.0075;
		break;
	case CHANNEL_5:
		Calibrated_Vbias = (vbias - 0.0186)/1.0044;
		break;
	case CHANNEL_6:
		Calibrated_Vbias = (vbias - 0.0142)/0.9975;
		break;
	default:
		break;
	}
#if PROBE_EDITION
  DAC856X_Write_Dac_Voltage(&dac1, machine->DAC_CH,
                             (Calibrated_Vbias - 1.5 + 12.5) /334*39);
#else
	switch (machine->param.BLE.Channel){
	case CHANNEL_1:
		Calibrated_Vbias = (vbias - 0.0193)/0.9967;
		break;
	case CHANNEL_2:
		Calibrated_Vbias = (vbias - 0.0146)/0.9965;
		break;
	case CHANNEL_3:
		Calibrated_Vbias = (vbias - 0.031)/0.9904;
		break;
	case CHANNEL_4:
		Calibrated_Vbias = (vbias - 0.0198)/0.9918;
		break;
	case CHANNEL_5:
		Calibrated_Vbias = (vbias - 0.0284)/0.9923;
		break;
	case CHANNEL_6:
		Calibrated_Vbias = (vbias - 0.0136)/0.9949;
		break;
	default:
		break;
	}
  DAC856X_Write_Dac_Voltage(&dac1, machine->DAC_CH,
                            (Calibrated_Vbias - 1.5 + 10) /8);
#endif
//	HAL_Delay(1);
  return 0;
}
float Get_Current(StateMachine *machine) {
	ADS125X_ReadChannelVolt(&machine->adc, machine->ADC_CH);
//	HAL_Delay(2);
  return ADS125X_ReadChannelVolt(&machine->adc, machine->ADC_CH) /
         machine->R_SENS;
}
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
